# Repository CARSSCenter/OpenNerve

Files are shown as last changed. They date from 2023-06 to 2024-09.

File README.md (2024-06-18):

# OpenNerve
This repository contains all files relevant to the design and manufacture of the CARSS OpenNerve Platform. For more information about the CARSS Center, visit our [website](https://sites.usc.edu/carss/). Documentation, explanations of files, and protocols for fabrication, testing, and inspection can be found in the associated [wiki](https://github.com/CARSSCenter/Admin/wiki).

# License
Unless otherwise specified, all information and documents found in this repository are licensed under the Creative Commons CC-BY-4.0 license.

Shield: [][cc-by]

This work is licensed under a
[Creative Commons Attribution 4.0 International License][cc-by].

[][cc-by]

[cc-by]: http://creativecommons.org/licenses/by/4.0/
[cc-by-image]: https://i.creativecommons.org/l/by/4.0/88x31.png
[cc-by-shield]: https://img.shields.io/badge/License-CC%20BY%204.0-lightgrey.svg

# Disclaimer
The contents of this repository are subject to revision. No representation or warranty, express or implied, is provided in relation to the accuracy, correctness, completeness, or reliability of the information, opinions, or conclusions expressed in this repository.

The contents of this repository (the “Materials”) are experimental in nature and should be used with prudence and appropriate caution. Any use is voluntary and at your own risk.

The Materials are made available “as is” by USC (the University of Southern California and its trustees, directors, officers, employees, faculty, students, agents, affiliated organizations and their insurance carriers, if any), its collaborators Med-Ally LLC and Medipace Inc., and any other contributors to this repository (collectively, “Providers”). Providers expressly disclaim all warranties, express or implied, arising in connection with the Materials, or arising out of a course of performance, dealing, or trade usage, including, without limitation, any warranties of title, noninfringement, merchantability, or fitness for a particular purpose.

Any user of the Materials agrees to forever indemnify, defend, and hold harmless Providers from and against, and to waive any and all claims against Providers for any and all claims, suits, demands, liability, loss or damage whatsoever, including attorneys' fees, whether direct or consequential, on account of any loss, injury, death or damage to any person or (including without limitation all agents and employees of Providers and all property owned by, leased to or used by either Providers) or on account of any loss or damages to business or reputations or privacy of any persons, arising in whole or in part in any way from use of the Materials or in any way connected therewith or in any way related thereto.

The Materials, any related materials, and all intellectual property therein, are owned by Providers.

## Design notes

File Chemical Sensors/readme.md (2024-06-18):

The chemical sensors include sensors to measure concentrations of acetylcholine (ACh), catecholamines such as dopamine, serotonin, and norepinephrine, and pH levels in the body. They are being developed at USC in the laboratory of [Dr. Maral Mousavi](https://sites.usc.edu/mousavi/).

Contributors: Mona Abdelmonem, Farbod Amir, Ali Soleimani, Maral Mousavi

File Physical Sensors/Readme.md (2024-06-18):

The Strain and Temperature sensors are being developed at USC in the laboratory of [Dr. Hangbo Zhao](https://sites.usc.edu/zhaogroup/).

Contributors: Xinghao Huang, Xuan Li, Hangbo Zhao

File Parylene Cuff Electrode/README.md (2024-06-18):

The Parylene C cuff electrode is designed for branch nerves less than 1mm in diameter. Design, fabrication, and testing are performed at USC at the [Biomedical Microsystems Laboratory](http://biomems.usc.edu/) of Dr. Ellis Meng.

Contributors: Brianna Thielen, Alberto Esteban Linares, Quentin Rezard, Ellis Meng

Please see the [Design](https://github.com/CARSSCenter/Device/tree/main/Parylene%20Cuff%20Electrode/Design) folder for design files and the [Fabrication and Packaging](https://github.com/CARSSCenter/Device/tree/main/Parylene%20Cuff%20Electrode/Fabrication%20and%20Packaging) folder for fabrication instructions (beginning with the "Full Fabrication Protocol", which references the "Thin Film Fabrication Protocol").

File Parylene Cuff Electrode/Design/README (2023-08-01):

All mask designs are included in a single DXF file as separate layers (metal, electrodes+edge, edge only)
- DXF units are microns
- The overall mask size is 5" x 5" square for lithography on a 4" wafer
- Designs are summarized in the accompanying PDF
- Built in AutoCAD 2022 S.51.0.0

All 3D renderings do not include metal patterning (only the Parylene backbone is modeled)
- STEP units are millimeters
- SLDPRT files include three configurations: flat (prior to thermoforming), 0.5 or 0.7 mm (thermoformed size), and 0.8 or 1.0 mm (largest implanted size)
- Built in SolidWorks Professional 2019 SP5.0

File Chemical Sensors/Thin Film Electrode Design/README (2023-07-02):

This folder contains files describing the design and manufacture of the thin-film Parylene C - Platinum electrodes used for testing the acetylcholine, catecholamine, pH, counter, and reference electrodes on the benchtop.
For initial tests, these electrodes were fabricated at the PIE Foundry at USC: https://piefoundry.usc.edu/

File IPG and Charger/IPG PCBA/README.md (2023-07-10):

# Overview

This folder contains files and information around the Printed Circuit Board contained inside the Implantable Pulse Generator (IPG). This PCB was designed for CARSS by [Medipace Inc.](https://www.medipaceinc.com/). Editable source files, generated using Altium, can be found in the Source Files folder.

# Design
The purpose of this PCBA is to regulate power, communication, neuromodulation, and biomarker sensing. For a detailed description of the circuit design, please see the [associated wiki page](https://github.com/CARSSCenter/Admin/wiki/PCBA).

# Status and updates
## 29 June 2023
The first revision of the PCBA has been taped out and assembled; testing is expected to be finished by the end of 2023.

Test Board rev1

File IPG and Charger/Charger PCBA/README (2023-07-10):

The charger PCBA is still under development

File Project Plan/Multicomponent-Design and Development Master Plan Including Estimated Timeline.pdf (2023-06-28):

Nest 1 3 - Multicomponent
Design and Developmet Master Plan Including Estimated Timeline
Task | Scheduled Completion Date | Comments
Year 1 | Nest 1 & 3 Combined
| Master Plan - Med-Ally | June-23
| Provide all related documents for deliverables | June-23
| Nest 1
| System Requirements Nest 1 | June-23
| Develop test Plans for proposed tests | June-23
| First Design of IPG and Charger | June-23
| Design Review - IPG | June-23
| Nest 3
| System Requirements Nest 3 | June-23
| First Design of PDMS cuff, SNS, EMG, ECG, and AMS leads | June-23
Year 2 | Nest 1 & 3 Combined
| Provide all related documents for deliverables | June-24
| Nest 1
| Develop test protocols for IPG mechanical tests | January-24
| Build IPG prototypes | January-24
| Complete mechanical testing for IPG and charger | June-24
| Nest 3
| Develop test plans for leads | February-24
| Develop custom test fixtures for leads | February-24
| Develop Test Protocols for Leads | June-24
| Build Lead prototypes | June-24
Year 3 | Nest 1 & 3 Combined
| Provide all related documents for deliverables | June-25
| Nest 1
| Build IPG prototypes | June-25
| Nest 3
| Complete Lead testing | February-25
| Build Lead prototypes | June-25

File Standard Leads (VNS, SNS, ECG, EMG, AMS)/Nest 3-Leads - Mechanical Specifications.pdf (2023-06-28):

### Nest 3 – Leads

Mechanical Specifications

Page 1 of 9

### 1.0 Purpose

The purpose of this document is to provide product specifications for applicable Hornet Lead Package

### 2.0 Scope

In scope for this document are the product specifications inclusive to the Hornet IPG and charger; as part of the CARSS program Nest 3. The CARSS program stands for Center for Autonomic Nerve Recording and Stimulation Systems. The CARSS is part of the NIH Human Open Research Neural Engineering Technologies (HORNET) initiative for open-architecture, open-source implantable neuromodulation system. This includes a collaborative team between University of Southern California (USC, Los Angeles, CA), Medipace Inc (Pasedena, CA), and Med-Ally, LLC (Goose Creek, SC). The purpose of the system which the IPG and charger is a portion of is to enable community-supported neurotechnology platform to remove technical and financial hurdles to getting access to implantable neuromodulation technologies. Nest 3 focuses on a set of 5 standard leads: SNS, PDMS cuff, ECG, EMG, and AMS lead.

### 3.0 Definitions

Abbreviation | Definition
BLE | Bluetooth Low Energy. Operates on frequencies: 2.400 GHz – 2.4835 GHz
Controller | A computing device capable of running the NBS-EPG and IPG Controller application(s) tailored for physicians, the patient, or researchers.
IPG | Implantable Pulse Generator
HW | Hardware
SW | Software
PCB | Printed Circuit Board
PSD | Product Specifications Document
GUI | Graphical User Interface

Lead Mechanical Specifications
Page 2 of 9

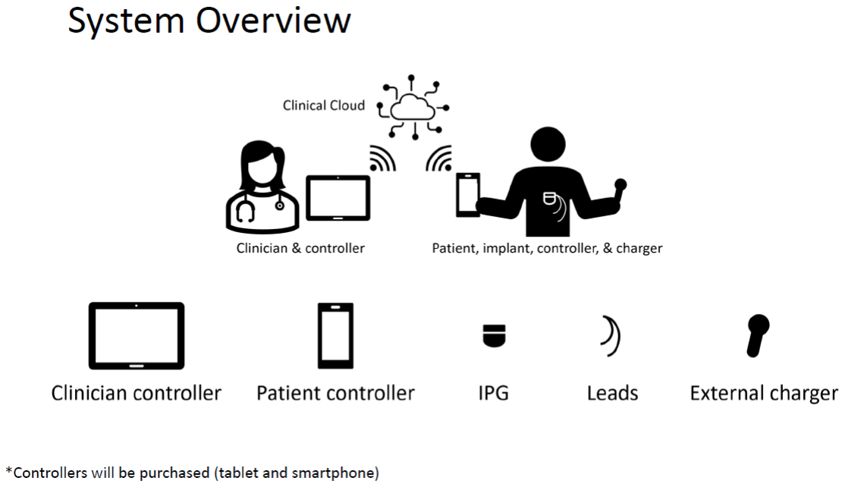
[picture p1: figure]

CONFIDENTIAL
All information contained in this document is confidential and is the sole property of Med-Ally Inc. Any reproduction in part or whole without the written permission of Med-Ally Inc. is prohibited.
Abbreviation | Definition
HIPAA | Health Insurance Portability and Accountability Act of 1996. U.S. legislation that provides data privacy and security for safeguarding medical information.
Wi-Fi | A facility allowing an electronic device to wirelessly transfer data or connect to the Internet using IEEE 802.11 standards. Operates on frequencies: 900 MHz, 2.4 GHz, 4.9 GHz, 5 GHz, 5.9 GHz and 60 GHz.
NIH | National Institute for Health
CARRS | Center for Autonomic Nerve Recording and Stimulation Systems
Hornet | Human Open Research Neural Engineering Technologies
Nest | Major component or module of the CARRS system

### 4.0 General Description of Product

The CARRS system is an open source system to enable developments in stimulation and sensing technologies. The system is capable of closed loop stimulation and sensing or can be used independently. The system components are: external charger and controller, implantable pulse generator, collection of interoperable and implantable leads.

Each portion of the CARSS system has been split into major components called nests. See

Page 3 of 9

figure below for details of major components or modules of the CARRS system:

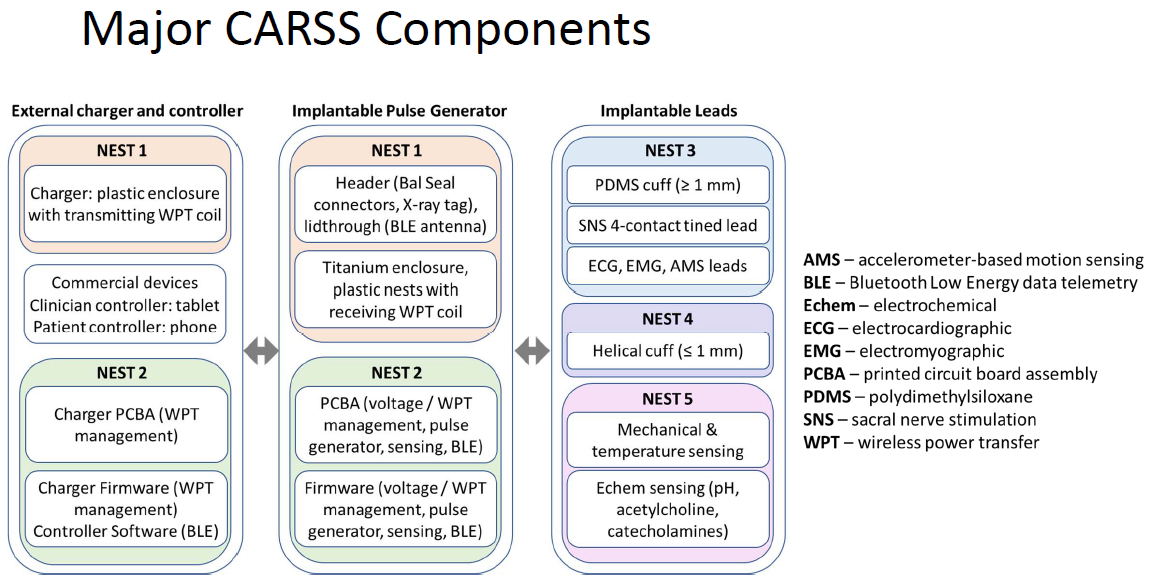
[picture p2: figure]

This document will only address Nest 1.
The IPG and charger for the CARRS system will be designed with the following engineering design principles as applicable:
- Material and component selection for maximizing the performance.
- Long-term reliability, redundancy, and fail-safe operations.
- Modularity, plug-and-play operation and off-the-shelf components.
- Preference for simpler and proven solutions over more complex and higher-risk ones.

### 6.0 Specifications

6.1 Leads Mechanical Specifications
PRD ID | Category | Specification Text
PRD-LDS-0001 | All | The leads are provided in the following lengths: 35 cm

Page 4 of 9

PRD ID | Category | Specification Text
| | 50 cm 50 cm 70 cm
PRD-LDS-0002 | All | The outside diameter of the leads shall be 1.27 mm diameter
PRD-LDS-0003 | All | The SNS, PDMS cuff, EMG, ECG, and AMS lead have 2 or 4 filar coiled leads with 0.70 mm pitch or greater.
PRD-LDS-0004 | All | The SNS, PDMS cuff, EMG, ECG, interconnect and AMS lead wire diameter is .102 mm/ 0.004” with 0.0127 mm/0.0005” thick coating.
PRD-LDS-0005 | All | The proximal contacts have 1.5mm length contacts.
PRD-LDS-0006 | All | The proximal set screw contact is 3mm in length.
PRD-LDS-0007 | All | Tines and trumpet anchor for anchoring can be added for each lead as needed.
PRD-LDS-0008 | All | The each connector utilizes a mechanism that holds the inserted lead in place. (e.g. set screw)
PRD-LDS-0009 | All | All the materials of the Lead Kit that are in contact with the body have been selected as known biocompatible.
PRD-LDS-0010 | All | The primary components for the Leads and interconnects shall be fabricated from the following materials: • Lead Body: Polyurethane, Pellethane 2363-55D • Proximal Inner Tube: PEEK • Distal Inner Tube: Polyurethane, Pellethane 2363-80A • Distal Electrodes: Platinum-Iridium (90/10) • Proximal Contacts: MP35N • Conductor Cable: PTFE coated Platinum-Iridium (80/20) • Setscrew: Titanium • Connector Block: MP35N

Page 5 of 9

PRD ID | Category | Specification Text
| | • Bal Seal connectors: MP35N and Pt-Ir • Silicone molded components Silicone Rubber -Med-4850, or similar • Connector block and set screw: 316L stainless steel • Misc Adhesives: Epoxy - Epotek 301, Silicone Rubber - Med-2000, urethane adhesive, silicone adhesive MED3-4213 • Suture: polypropylene or silk • Tines: pellethane • Suture Needle, crimp tubes: 316L Stainless Steel
PRD-SNS-0001 | SNS | SNS leads have electrodes on the distal end that are 3 mm in length with 3 mm space between electrodes
PRD-SNS-0002 | SNS | Up to 4 tines in series are added to the lead body to aid in lead retention and stability in vivo.
PRD-SNS-0003 | SNS | The lead systems incorporates a radio-opaque marker at the distal array in the form of platinum electrodes
PRD-SNS-0004 | SNS | The leads with a stylet inserted is able to pass completely through an 18-gauge needle
PRD-INT-0001 | Interconnect | The distal connector of the interconnect incorporates a connector block and set screw for securing the lead to the connector
PRD-INT-0002 | Interconnect | The distal connector of the interconnect accommodates two bipolar male connectors.
PRD-INT-0003 | Interconnect | The proximal connector of the interconnect interfaces with a quadipolar Sygnus Neuro Bal Seal connector in the IPG header.
PRD-INT-0004 | Interconnect | The interconnect connection portion is smaller than 0.5” X 1.5” X 0.5”
PRD-EMG-0001 | EMG | The EMG lead incorporates a Suture style needle

Page 6 of 9

PRD ID | Category | Specification Text
PRD-EMG-0002 | EMG | The EMG lead incorporates a suture connecting the needle to the stimulating portions of the lead
PRD-EMG-0003 | EMG | The EMG lead contains a single stimulating or sensing electrode
PRD-EMG-0004 | EMG | The EMG lead contains a Tumpet anchor to anchor electrode in place
PRD-EMG-0005 | EMG | The EMG lead interfaces with the bipolar connection.
PRD-EMG-0006 | EMG | The insertion needle length on the EMG lead is 32 mm
PRD-ECG-0001 | ECG | The ECG lead has two electrodes that can be 3mm to 100 mm apart.
PRD-ECG-0002 | ECG | The ECG lead has two anchor points: one at the end of the lead and the second proximal to the first electrode
PRD-ECG-0003 | ECG | The ECG lead interfaces with the bipolar connection
PRD-CUF-0001 | Cuff | The cuff electrode will have an inner diameter that accommodates nerves 2.5-5.5 mm in diameter – nominally 3.58 mm nerve.
PRD-CUF-0002 | Cuff | Cuff leads shall have two electrodes for bipolar stimulation.
PRD-CUF-0003 | Cuff | Cuff length along the nerve is 10 mm
PRD-CUF-0004 | Cuff | Lead exits cuff parallel to nerve
PRD-CUF-0005 | Cuff | Cuff electrode spacing is 2.5mm
PRD-CUF-0006 | Cuff | Electrodes are located 2.25mm inboard from edge of cuff
PRD-CUF-0007 | Cuff | Silicone cuff thickness is 1 mm
PRD-CUF-0008 | Cuff | Cuff includes dual sutures 35 mm long and 0.2mm diameter

Page 7 of 9

6.2 Testing Requirements
PRD ID | Specification Text
PRD-LDS-0011 | The leads contacts are electrically isolated to prevent interference between signals.
PRD-LDS-0012 | The Leads and Extensions shall be designed to withstand the following flexure cycles: -The Lead and Extension Connector shall withstand a minimum of 82,000 flex cycles. -The Lead and Extension body sections shall withstand a minimum of 47,000 flex cycles. Reference: EN45502-2-1 CENELEC Standard for Brady Pacemakers Testing will be performed per EN4552-2-1/ISO14708-2: 23.5.
PRD-LDS-0013 | Once the lead is locked in place into the IPG port or extension with the set screw fully torqued, the retention force of the lead shall be 10 N minimum along the lead axis relative to the connector. This retention force may exceed the destructive pull force of the inserted lead. EN45501-1 section 23.6 / ISO 14708-2: 23.6
PRD-LDS-0014 | When a tensile force of 5N is applied for 2 seconds along the main axis the of the lead or extension the assembly must not electrically and/or mechanically fail. ISO 14708-2: 23.3
PRD-LDS-0015 | Lead Insertion/Withdrawal Force Connector: The insertion and withdrawal force of a lead connector array into the IPG port connector or lead Extension port shall not exceed 2.2 lbs (9.8 N).
PRD ID | Category | Specification Text
PRD-AMS-0001 | AMS | The AMS lead is a quadripolar lead
PRD-AMS-0002 | AMS | The AMS lead has three suture points to anchor AMS distal end

Page 8 of 9

PRD ID | Specification Text
PRD-LDS-0016 | The interface between the extension distal connector body and a connected component shall not electrically and/or mechanically fail when tensile force of 2.2 lbf (9.8N) is applied between the components or across theirinterface. Deformation of componentsis allowable. Fracture of tubing orseparation of tubing from a component is not allowable. Examples of tensile force arrangements between an attached component and the Extension body.
PRD-LDS-0017 | The resistance for each connection in the distal connector shall remain ≤1000 Ohms and must not mechanically fail when bent 45°±2° off the main axis in any direction ISO 14708-2: 6.2.3
PRD-LDS-0018 | All the leads in the Leads Kit shall observe industry standard wiring practices for this type of application. The contact female connectors at the distal end and male contacts at the proximal end shall be connected through a one-to-one connection.
PRD-LDS-0019 | The proximal contact arrays of the Lead shall withstand 20 insertion and withdrawal cycles into the connector on the interconnect cable without causing physical or functional damage to the Lead.
PRD-LDS-0020 | The proximal contact arrays of the Lead and Extension shall withstand 20 insertion and withdrawal cycles into the port connector on the IPG without causing physical or functional damage to the Lead.
PRD-LDS-0021 | The lead assemblies should be able to withstand (function after experiencing) the following:

Page 9 of 9

PRD ID | Specification Text
| Accelerated aging per ISO 14708-1:19-1
PRD-LDS-0022 | When the lead or Extension assembly is dry in air, the electrical leakage between conductors at 100 ± 5 Volts DC shall be ≤10 microamperes. ISO 14708-2: 16.1
PRD-LDS-0023 | When the lead or Extension assembly is dry in air, the electrical leakage from any conductor to the outside lead body at 1000 ± 50 Volts DC shall be ≤0.75 microamperes per mm². ISO 14708-2: 16.2

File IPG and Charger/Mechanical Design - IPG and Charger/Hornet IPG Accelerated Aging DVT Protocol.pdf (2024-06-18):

### Hornet IPG

### Accelerated Aging Test Protocol

Effective Date: | Rev: | Pg. 1 of 19

CONFIDENTIAL
All information contained in this document is confidential and is the sole property of Med-Ally Inc. Any reproduction in part or whole without the written permission of Med-Ally Inc. is prohibited

1 Purpose
This protocol prescribes methods and records results to ensure the Hornet IPG adheres to accelerated aging standards. This protocol is based on ISO standards with reference to specific methods established at Med-Ally. This protocol is intended to be edited to meet the needs of each project at the time of execution without requiring revision of the template.
2 Scope
This document details methods for verification testing to ensure the devices continue to meet standards and requirements for the anticipated lifecycle of the device, and forms to record testing results. Section 8, Approvals, is intended to be repeatedly completed as testing stages of accelerated aging or real time samples and functional testing is completed.
3 References
Document No. | Title
ISO 14708-1: 19-1 | Implants for surgery – Active implantable medical devices – Part 1: General requirements for safety, marking and for information to be provided by the manufacturer
BS EN ISO 11607-1:2020 | Packaging for terminally sterilized medical devices, Part 1: Requirements for materials, sterile barrier systems, and packaging
ASTM F1980-16 | Standard Guide for Accelerated Aging of Sterile Barrier Systems for Medical Devices

### 4 Appendices

Appendix: | Title
A | Characterization of Material
B | Accelerated Aging Interval Record
C | Performance Test Requirements
D | Performance Testing Record
E | Serial Number Log
F | Real Time Aging Record
G | Testing Deviation Log
H | Additional Notes Area (if required)

### 5 Definitions

### Hornet IPG

### Accelerated Aging Test Protocol

Effective Date: | Rev: | Pg. 2 of 19

CONFIDENTIAL
All information contained in this document is confidential and is the sole property of Med-Ally Inc. Any reproduction in part or whole without the
Abbreviation or Term | Definition
DVT | Design Verification Test
IPG | Implantable Pulse Generator
DUT | Device Under Test
TAA | The elevated temperature at which the aging study is conducted, and it may be based on the estimated storage temperature, estimated usage temperature, or both
AAF | Accelerated Aging Factor; a correlation between the number of real time days to the number of simulated accelerated days, where 1 AAF = X RT days (reference calculations in the protocol for more information)
AAT | The length of time the accelerated aging is conducted
TRT | Storage temperature of real-time aging (RT) samples that represent storage conditions
Q10 | An aging factor for 10 ⷪC increase or decrease in temperature
Tm | Temperature at which a material melts
Tg | Glass transition temperature
Tα | Alpha temperature, heat distortion temperature
RT | Storage time of samples at ambient conditions
RT# | Number of real time days; desired real time shelf life duration or interval
AATRT# | Number of Accelerated Aging days, representing (real time * AAF) days in an interval period
Morphology | Examples include glassy amorphous, semi-crystalline, highly crystalline, % crystallinity, size, shape, structure, etc.

### Hornet IPG

### Accelerated Aging Test Protocol

Effective Date: | Rev: | Pg. 3 of 19

CONFIDENTIAL
All information contained in this document is confidential and is the sole property of Med-Ally Inc. Any reproduction in part or whole without the

### 6 Testing Protocol

6.1 Per the applicable standards, accelerated aging methods shall be used to determine any effects the passage of time may have on packaging components. Product requirement documents will establish the anticipated lifecycle of the sterlie packaging system, and be used as guidance for accelerated aging parameters. Record the following information and perform calculations to determine accelerated aging parameters:

6.1.1 | The Hornet IPG PN: will be tested to simulate 2 years using accelerated aging.
6.1.2 | List of Device Materials and Heat sensitive components: Part Number: __________________________________ Part Number: __________________________________ Part Number: __________________________________ Part Number: __________________________________ Part Number:__________________________________ Part Number: __________________________________ Part Number: __________________________________ Part Number: __________________________________ Part Number: __________________________________ Part Number: __________________________________ Part Number:__________________________________ Part Number: __________________________________ Part Number: __________________________________ Part Number: __________________________________ Complete Appendix A, Characterization or Materials, for each part unique part number of the device.

### Hornet IPG

### Accelerated Aging Test Protocol

Effective Date: | Rev: | Pg. 4 of 19

CONFIDENTIAL
All information contained in this document is confidential and is the sole property of Med-Ally Inc. Any reproduction in part or whole without the
Initial:__________________________ | Date:__________________________
6.1.3 | Long Term Storage Ambient Temperature* (TRT): 37 ⷪC
6.1.4 | Accelerated Aging Temperature* (TAA) : 55 ⷪC
6.1.5 | Q Factor* (Q10): 2.0
*Use 2.0 unless otherwise specified 6.1.6 Calculate Accelerated Aging Factor. Where: AAF = Accelerated Aging Factor
TAA = Accelerated Aging Temperature TRT = Ambient storage Temperature Q10 = Q Factor

AAF = Q10 [(TAA – TRT)/10]

AAF = 2.0[ ( 55 minus 37) divided by 10)] AAF = 2.0[ (18) divided by 10)]
AAF = 2.0[ 1.8 ]
AAF = 3.48 Days
6.1.7 | Desired Real Time Intervals (RT#):
| RT1: 90 Days (3 months) RT2: 182 Days (6 months) RT3: 365 Days (12 Months) RT4: 730 Days (24 Months) RT5: 1095 Days (36 Months) RT6: 1460 Days (48 Months) RT7: 1825 Days (60 Months)
6.1.8 | Accelerated Aging Time (AAT) for each Desired Real Time interval (Round to nearest
whole number):
| RT1 = 90 AATRT1 = RT1 Days / AAF AATRT1 = 90 divided by 3.48 AATRT1 = 26 Days
| RT2 = 183 AATRT2 = RT2 Days / AAF

### Hornet IPG

### Accelerated Aging Test Protocol

Effective Date: | Rev: | Pg. 5 of 19

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

AATRT2 = 183 divided by 3.48
AATRT2 = 53 Days

RT3 = 365
AATRT3 = RT3 Days / AAF
AATRT3 = 365 divided by 3.48 AATRT3 = 105 Days
RT4 = 730
AATRT4 = RT4 Days / AAF
AATRT4 = 730 divided by 3.48
AATRT4 = 210 Days

Print a copy of Appendix B, Accelerated Aging Interval Record, and complete the AAT information (top portion) for each desired interval required. Print an additional copy for RT0, to establish baseline testing results.

Initial:_______________________ | Date:________________________
6.1.9 | Performance Testing Requirements:
Complete Appendix C, Performance Test Requirements, to outline the tests to be performed by all accelerated and real time performance testing. Tests selected for evaluation should challenge the materials or device functionality that is most critical or most likely to fail as a result of aging.
Initial:____________________ | Date:___________________

6.2 Document the required number of RT samples below:

Total Real Time Sample Number:__________________________

Complete a copy of Appendix F for all Reat Time Aging test intervals, top portion only. Initial:____________________________ Date:_________________________

6.3 Total Sample Number:__________________________, as required per XXXX Hornet IPG and Charger Test Plan

### Hornet IPG

### Accelerated Aging Test Protocol

Effective Date: | Rev: | Pg. 6 of 19

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

6.4 Finished Device Drawing Number(s):__________________________________________

Initial:__________________ Date:_________________
6.5 Approval:

A representative from QA must review and approve the specification information to ensure accuracy of test protocol.

Quality Review Checklist:

Life-cycle Requirements | Initial____________ | Date:________________

Appendix A (Initial & Date on form) Qty:__________ Initial____________Date:________________

AAF Calculation Verification | Initial____________ | Date:________________
Desired RT Interval Verification | Initial____________ | Date:________________
AATRT# Calculation Verification | Initial____________ | Date:________________
Sample Number Verification | Initial____________ | Date:________________

Appendix B (Top Portion) Qty:__________ Initial____________Date:________________
Appendix C Performance Test Requirements | Initial____________ | Date:______________
Appendix F Real Time Aging Record (Top Portion) Initial____________ | Date:______________

Notes:_____________________________________________________________________

__________________________________________________________________________

__________________________________________________________________________

__________________________________________________________________________

Quality Approval to Execute Testing:

Signature:______________________________________ Date:_____________________

### Hornet IPG

### Accelerated Aging Test Protocol

Effective Date: | Rev: | Pg. 7 of 19

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

Due to duration of testing and costs, customer review and approval is required prior to starting Accelerated Aging. Customer Approval:
Print Name:____________________________________________

Position:__________________________________________

Signature:______________________________________ Date:_____________________ 6.6 Sample Generation

6.6.1 Describe the origin of the samples used. If new samples where created for this test, describe any deviations, if applicable, that may impact testing. Include work order number if available.

| ____________________________________________________________________
| ____________________________________________________________________
| ____________________________________________________________________
| ____________________________________________________________________
| ____________________________________________________________________
| ____________________________________________________________________
| ____________________________________________________________________
| ____________________________________________________________________
| ____________________________________________________________________
| ____________________________________________________________________
| ____________________________________________________________________
| ____________________________________________________________________
| Initial:___________________ Date:__________________

### Hornet IPG

### Accelerated Aging Test Protocol

Effective Date: | Rev: | Pg. 8 of 19

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

6.7 Sterilization
6.7.1 Submit all samples for sterilization per standard procedure:

Work Instruction:____________________________________

Shipping Date:______________________________________

Initial:_____________________ | Date:____________________
6.7.2 | Perform visual inspection on all samples for anomalies, damage, and paperwork
completeness. Attach sterilization records to this protocol.

Post Sterilization Return Date:______________________

Visual Inspection- Initial:_____________________ Date:_________________

Paperwork Verification- QA Initial:____________________Date:________________ 6.8 Equipment Information:

Controlled Environment Chamber or Bath:_________________________

Temperature Controller:________________________

Last Cal:__________________________ Cal Due:___________________

Timer:____________________________

Last Cal:__________________________ Cal Due:___________________

Thermal Logger:____________________________

### Hornet IPG

### Accelerated Aging Test Protocol

Effective Date: | Rev: | Pg. 9 of 19

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

Last Cal:__________________________ Cal Due:___________________

Notes:______________________________________________________________

____________________________________________________________________

____________________________________________________________________

____________________________________________________________________

Initial:_____________ Date:_______________
6.9 | Accelerated Aging and Real Time Testing:
6.9.1 | Complete Appendix D, Serial Number Log to designate devices for their intended testing
purpose. Reference the Testing Protocol section for required sample numbers in each category.
| Operator Initial:___________________ Date:____________________
6.9.2 | Place all real time samples into storage location. Record the Start date, andticipated
finsh date, and initial and date on all Appendix F, Real time Aging records to record real time aging initiation.
| Operator Initial:___________________ Date:____________________
6.9.3 | Place all accelerated aging samples into the BATH 0.9% sodium chlorine, ensuring the
temperature setpoint matches requirements. Record the Actual Start Date and Anticipated Finish Date for all Appendix B, Accelerated Aging Interval Record for all AATRT# forms to record accelerated aging initiation. Ensure thermologger is recording data at a rate >= 1 sample per minute.
Solution Part Number:_____________________________

Solution Lot Number:______________________________

Solution Expiration Date:___________________________

### Hornet IPG

### Accelerated Aging Test Protocol

Effective Date: | Rev: | Pg. 10 of 19

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

Operator Initial:___________________ Date:____________________

6.9.4 RT0 devices, as designated by Appendix E, Serial Number Log, may be tested immediately per requirements of Appendix C, Performance Testing Requirements, and recorded on the form in Appendix D, Performance Testing Record. Attach any reports generated by required testing to Appendix D, and submit the forms to QA for review upon completion.

Operator Initial:___________________ Date:____________________

6.9.5 Enter the Next Anticipated completion dates for AATRT# and RT#. Upon completion of required durations, review data logs to ensure accelerated aging devices have completed the required time period. Print an attach verification data to this protocol as it becomes available. Complete copies of Appendix D, Performance Testing Record for each batch of parts that meet accelerated or real time aging required durations.
In the event of power disruptions or data loss, complete Appendix G, Testing Deviation Record, to amend the duration requirements and change the anticipated completion dates.
Note: An NCR is NOT required if time is extended equal to the power out period or period of data loss if the deviation form is completed and attached, and no risk from the adverse event is expected to impact device performance.

The steps in this section shall be repeated until all aging durations are completed, and reviewed in the Approvals section.

### Hornet IPG

### Accelerated Aging Test Protocol

Effective Date: | Rev: | Pg. 11 of 19

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

### 7 Approvals –

### Note: This approval page is intended to be completed for each Accelerated Aging or

Real time data set. Release the protocol and up-rev with each completed aging stage.

### 7.1 Describe the functional testing stage being completed (AAT=RTx; Rtx, Etc):

### ____________________________________________________________

### ____________________________________________________________

### 7.2 Verify testing results meet drawing requirements and test standards

### Initial___________________ Date________________ 7.3 Quality Approval

7.3.1 | Review Protocol Completeness
7.3.2 | Review Appendix A: Characterization of Material
7.3.3 | Review Appendix B: Accelerated Aging Interval Record
7.3.4 | Review Appendix C: Performance Testing Requirements
7.3.5 | Review Appendix D: Performance Testing Record
7.3.6 | Review Appendix E: Serial Number Log
7.3.7 | Review Appendix F: Real Time Aging Record
7.3.8 | Review Appendix G: Testing Deviation Record
7.3.9 | Review Appendix H: Additional Notes

### 7.3.10 Ensure records support all required real time and accelerated aging

durations.

### Signature:_______________________________ Date:_____________________ 7.4 Other Approval (If required):

### Signature:_______________________________ Date:_____________________ 7.5 Notes (if required): _________________________________________________________________

### _________________________________________________________________

### _________________________________________________________________

### _________________________________________________________________

### Hornet IPG

### Accelerated Aging Test Protocol

Effective Date: | Rev: | Pg. 12 of 19

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

### Appendix A: Characterization of Material

### Part Number:_______________________________

### Part Description:_____________________________

### Composition:________________________________________________________________

### Morphology:________________________________________________________________

Tm=___________ ⷪC | Tg=___________ ⷪC | Tα=___________ ⷪC

Additive, processing agents, catalysts, lubricants, residual solvents, corrosive gasses, and

### fillers, or other notes:

### __________________________________________________________________________

### __________________________________________________________________________

### __________________________________________________________________________

### __________________________________________________________________________

### __________________________________________________________________________

### __________________________________________________________________________

### __________________________________________________________________________

### __________________________________________________________________________

### Suggested Max Temperature:_________________ ⷪC

### Signature:_________________________________ Date:______________________

### QA Initial:________________________ Date:______________________

### Hornet IPG

### Accelerated Aging Test Protocol

Effective Date: | Rev: | Pg. 13 of 19

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

### Appendix B: Accelerated Aging Interval Record

### Finished Assembly Drawing Number:______________________________________

### AATRT#:__________________________ Real Time Duration:___________________days

### Accelerated Aging Time:____________days Sample Number:____________

### Temperature Set Point:_____________

### Print Name:______________________________________________________

### Signature:__________________________________ Date:______________________

### Actual Start Date:_______________________ Initial:____________ Date:___________

### Anticipated Finish Date:_______________________

### Deviations:

### __________________________________________________________________________

### Notes: __________________________________________________________________________

### __________________________________________________________________________

Finish Date:_______________________ | Sample Number:____________
Attach Thermologger Data (Check): ____ | Total Accelerated Aging Time:___________

### Minimum Duration at Accelerated Temperature Verified (check): ____

### Print Name:______________________________________________________

### Signature:__________________________________ Date:______________________

### Hornet IPG

### Accelerated Aging Test Protocol

Effective Date: | Rev: | Pg. 14 of 19

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

### Appendix C: Performance Testing Requirements

### Visual Inspection Requirements: __________________________________________________________________________

### __________________________________________________________________________

### __________________________________________________________________________

### __________________________________________________________________________

### __________________________________________________________________________

### Functional Testing Requirements: __________________________________________________________________________

### __________________________________________________________________________

### __________________________________________________________________________

### __________________________________________________________________________

### __________________________________________________________________________

### Bench Testing Requirements: __________________________________________________________________________

### __________________________________________________________________________

### __________________________________________________________________________

### __________________________________________________________________________

### __________________________________________________________________________

### Operator Signature:____________________________ Date:__________________________

### Quality Signature:______________________________ Date:____________Page___ of____

### Hornet IPG

### Accelerated Aging Test Protocol

Effective Date: | Rev: | Pg. 15 of 19

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

### Appendix D: Performance Testing Record

### Serial Number

### Visual Inspection Pass/ NCR#

### Functional Inspection Pass/ NCR#

### Bench Testing Pass/ NCR#

### Notes:

### Operator Signature:____________________________ Date:__________________________

### Quality Signature:______________________________ Date:____________Page___ of____

### Hornet IPG

### Accelerated Aging Test Protocol

Effective Date: | Rev: | Pg. 16 of 19

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

### Appendix E: Serial Number Log

Serial Number | Select One | RT# | Testing Duration (Days) | Start Date
Accelerated Aging | Real Time Aging

### Operator Signature:____________________________ Date:__________________________

### Quality Signature:______________________________ Date:____________Page___ of____

### Hornet IPG

### Accelerated Aging Test Protocol

Effective Date: | Rev: | Pg. 17 of 19

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

### Appendix F: Real-Time Aging Record

### Finished Assembly Drawing Number:______________________________________

### RT#:____________________________Duration:___________________days

### Sample Number:____________ Ambient Start Temperature: ________

### Print Name:______________________________________________________

### Signature:__________________________________ Date:______________________

### Start Date:_______________________Anticipated Finish Date:____________

### Initial:___________________________Date:_________________

### Deviations:

### __________________________________________________________________________

### __________________________________________________________________________

### Notes: __________________________________________________________________________

### __________________________________________________________________________

### __________________________________________________________________________

### Ambient Finish Temperature:______________________

### Actual Finish Date:_______________________ Sample Number:____________

### Total Time Elapsed:_________________ days

### Print Name:______________________________________________________

### Signature:__________________________________ Date:______________________

### Hornet IPG

### Accelerated Aging Test Protocol

Effective Date: | Rev: | Pg. 18 of 19

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

### Appendix G: Testing Deviation Record

### Date of Deviation:_______________________________________

### Cause of Deviation:_________________________________________________________

### __________________________________________________________________________

### __________________________________________________________________________

### Current RT#:____________

### End of Deviation Date:__________________________________

### Prior anticipated RT# Aging Completion Date:_________________________

### New anticipated RT# Aging Completion Date:__________________________

### NCR:____________________________ if applicable*

*NCR is not required if the only impact is completion extension.

### Engineer Name:_____________________________

### Engineer Signature:__________________________ Date:______________________

### QA Representative Name:____________________________________

### QA Signature:_______________________________ Date:______________________

### Hornet IPG

### Accelerated Aging Test Protocol

Effective Date: | Rev: | Pg. 19 of 19

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

### Appendix H: Additional Notes (if required). Notes may be typed or hand written:

### Signature:_____________________________ Date:____________ Page___ of____

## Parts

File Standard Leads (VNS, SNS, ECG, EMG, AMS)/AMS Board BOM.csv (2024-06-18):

Name | Description | Designator | Manufacturer 1 | Manufacturer Part Number 1
ZRB15XR61A106ME01D | Capacitor, 10uf, X5R, 10V, 20%, 0402, Implant-grade | C200 | Murata | ZRB15XR61A106ME01D
GCM155R71C104KA55 | Capacitor, 0.1uF, X7R, 16V, 10%, 0402, Implant-grade | C201 | Murata | GCM155R71C104KA55J
MIS2DHTR | Analog Circuit, Accelerometer, LGA-12 | U200 | STMicroelectronics | MIS2DHTR

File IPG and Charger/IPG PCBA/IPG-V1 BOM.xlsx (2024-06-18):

Quantity | Designator | Description | Manufacturer | Manufacturer Part Number
8 | C100, C101, C104, C105, C210, C211, C215, C219 | Ceramic Capacitor, Multilayer, Ceramic, 25V, 5% +Tol, 5% -Tol, C0G, 30ppm/Cel TC, 0.000012uF, Surface Mount, 0201 | Murata | GRM0335C1E120JA01D
15 | C102, C103, C115, C118, C119, C213, C306, C317, C319, C501, C503, C504, C600, C1201, C1203 | Capacitor, 4.7uF, X5R, 16V, 10%, 0603, Implant-grade | Murata | GRM188R61C475KE11
49 | C106, C107, C108, C109, C110, C111, C112, C113, C114, C116, C120, C214, C216, C307, C500, C502, C507, C508, C509, C510, C511, C512, C602, C700, C701, C702, C703, C704, C800, C801, C807, C808, C815, C816, C819, C820, C821, C822, C901, C903, C905, C908, C1101, C1200, C1202, C1204, C1207, C1300, C1301 | Ceramic Capacitor, Multilayer, Ceramic, 25V, 10% +Tol, 10% -Tol, X5R, 15% TC, 0.1uF, Surface Mount, 0201 | Murata | GRM033R61E104KE14J
7 | C117, C218, C400, C420, C1102, C1205, C1206 | Ceramic Capacitor, Multilayer, Ceramic, 16V, 20% +Tol, 20% -Tol, X5R, 15% TC, 1uF, Surface Mount, 0201 | Murata | GRM033R61C105ME15D
1 | C200 | Capacitor, 0.8pF, Silicon RF, 200V, Tolerance 0.05pF, 0402, Implant-grade | Kyocera AVX | 600L0R8AT200T
1 | C201 | Capacitor, 1pF, RF Capacitors, 200V, Tolerance 0.01pF, 0402, Implant-grade | Kyocera AVX | 600L1R0AT200T
1 | C217 | Ceramic Capacitor, Multilayer, Ceramic, 25V, 10% +Tol, 10% -Tol, X7R, 15% TC, 0.0001uF, Surface Mount, 0201 | Murata | GRM033R71E101KA01D
2 | C300, C301 | Capacitor, 27nF, C0G, 100VDC, 2%, 0805, Implant-grade | Murata | GRM2195C2A273GE01D
2 | C302, C303 | Capacitor, 4.7nF, C0G, 25V, 1%, 0603, Implant-grade | KEMET | C0603C472F3GECTU
1 | C304 | Ceramic Capacitor, Multilayer, Ceramic, 25V, 5% +Tol, 5% -Tol, C0G, 30ppm/Cel TC, 0.000033uF, Surface Mount, 0201 | Murata | GRM0335C1E330JA01D
5 | C310, C311, C318, C505, C506 | Capacitor, 4.7uF, X7S, 35V, 10%, 0805, Implant-grade | Murata | GCM21BC7YA475KE36L
2 | C315, C316 | Capacitor, 0.022uF, X7R, 50V, 10%, 0402, Implant-grade | Murata | GCM155R71H223KA55
2 | C417, C422 | Capacitor, 0.1uF, X7R, 16V, 10%, 0402, Implant-grade | Murata | GCM155R71C104KA55
2 | C419, C423 | Ceramic Capacitor, Multilayer, Ceramic, 25V, 10% +Tol, 10% -Tol, X7R, 15% TC, 0.00047uF, Surface Mount, 0201 | Murata | GCM033R71E471KA03D
1 | C601 | Capacitor, 10uf, X5R, 10V, 20%, 0402, Implant-grade | Murata | ZRB15XR61A106ME01D
2 | C802, C804 | Capacitor, 0.33uF, X7S, 16V, 10%, 0402 | TDK | CGA2B1X7S1C334K050BC
5 | C803, C805, C810, C814, C823 | Ceramic Capacitor, Multilayer, Ceramic, 25V, 10% +Tol, 10% -Tol, X7R, 15% TC, 0.001uF, Surface Mount, 0201 | Murata | GRM033R71E102KA01J
1 | C806 | Capacitor, 1500pF, X7R, 50V, 10%, 0402 | Murata | GCM155R71H152KA37D
2 | C809, C827 | Ceramic Capacitor, Multilayer, Ceramic, 6.3V, 20% +Tol, 20% -Tol, X5R, 15% TC, 1.5uF, Surface Mount, 0201 | Murata | GRM033R60J155ME14D
4 | C811, C812, C824, C825 | Capacitor, 470nF, X5R, 6.3V, 10%, 0201, Implant Grade | Murata | GRT033R60J474KE01D
2 | C813, C828 | 68 pF ±5% 50V Ceramic Capacitor C0G, NP0 0201 (0603 Metric) | Murata Electronics | GRM0335C1H680JA01D
2 | C817, C818 | Capacitor, 2.2uF, X7R, 16V, 10%, 0603, Implant-grade | Murata | GRM188Z71C225ME43J
2 | C826, C829 | 270 pF ±5% 25V Ceramic Capacitor C0G, NP0 0201 (0603 Metric) | Murata Electronics | GRM0335C1E271JA01D
9 | C900, C902, C904, C906, C907, C909, C910, C911, C912 | Capacitor, 10uF, X5R, 50V, 10%, 0805 | Murata | GRM21BR61H106ME43L
16 | C1000, C1001, C1002, C1003, C1004, C1005, C1006, C1007, C1008, C1009, C1010, C1011, C1012, C1013, C1014, C1015 | Capacitor, 680pF, C0G, 100V, 5%, 0402 | TDK | C1005C0G2A681J050BE
1 | C1016 | Capacitor, 68pF, C0G, 25V, 5%, 0201, Implant-grade | Murata | GRT0335C1E680JA02D
10 | D300, D301, D305, D306, D400, D420, D502, D503, D505, D506 | Schottky, 40V, 500mA, 530mV, SOD-523 | ON Semiconductor | NSR05T40XV2T5G
1 | D307 | Zener Diode 10 V 300 mW ±2% Surface Mount DFN1006-2A 0402 | Vishay | BZX884B10L-G3-08
7 | D419, D421, D422, D423, D424, D600, D601 | Schottky, 30V, 100mA, 385mV, 200mW, SOD-923 | ON Semiconductor | NSR0130P2T5G
16 | D800, D801, D802, D803, D804, D805, D806, D807, D808, D809, D810, D811, D812, D813, D814, D815 | Diode | Nexperia | BAS116LS-QYL
17 | D1000, D1001, D1002, D1003, D1004, D1005, D1006, D1007, D1008, D1009, D1010, D1011, D1012, D1013, D1014, D1015, D1016 | Diode ESD (Bi-directional) | Nexperia | PESD5V0S1BLD,315
2 | D1101, D1102 | ESD TVS DIODE 3.3VWM 6.2VC 0402C | Comchip Technology | CPDQC3V3T-HF
1 | D1201 | TVS DIODE 5.5VWM 6TSOP | Nexperia | IP4220CZ6F
1 | D1202 | LED, GREEN, SMD, 0603, 3.2V, 20mA | Lite-On Inc. | LTST-C191TGKT
1 | D1203 | LED, RED, SMD, 0603, 2V, 30mA | Lite-On Inc. | LTST-C191KRKT
1 | D1204 | LED, ORANGE, SMD, 0603, 2V, 30mA | Lite-On Inc. | LTST-C191KFKT
2 | F400, F401 | Fuse, 750mA, 63V, 1206 | Littelfuse | 0440.750WR
4 | J100, J102, J201, J202 | 0.025" SQ Post Header, Through-hole, Vertical, -55 to 125 degC, 2.54 mm Pitch, 6-Pin, Male, RoHS | Samtec | TSW-106-07-G-S
2 | J101, J200 | Connector, 1.27 mm, 2x5, Male, TH | Samtec | FTSH-105-01-F-D-K
1 | J203 | RF Connector, 1 Contact(s), Male, Board Mount, Surface Mount Terminal, Receptacle | Hirose | U.FL-R-SMT-1(10)
5 | J302, J421, J424, J1101, J1202 | Board Connector, 4 Contact(s), 1 Row(s), Male, Straight, 0.1 inch Pitch, Solder Terminal, Black Insulator, Receptacle | Samtec | TSW-104-07-G-S
17 | J1017, J1018, J1019, J1020, J1021, J1022, J1023, J1024, J1025, J1026, J1027, J1028, J1029, J1030, J1031, J1032, J1033 | Connector, Bannana Tip, Through Hole, Rodent Study lead connector | Cinch Connectivity Solutions Johnson | 105-0753-001
1 | J1201 | CONN RCP USB3.1 TYPEC 24P SMD RA | Molex | 1054500101
1 | L100 | Inductor, 2.2uH, 1.76A, 1008 | TDK | VLS252010HBX-2R2M-1
1 | L101 | Inductor, Unshielded, 33nH, 350mA, 0402 | Murata | LQG15HS33NJ02D
1 | L200 | Inductor, 3.9nH, 1.95A, 2%, 0402 | Murata | LQW15AN3N9G80D
1 | L201 | Inductor, 1.8nH, 0.46A, Tolerance 0.2 nH, 0402 | Murata | LQW15AN1N8C00D
2 | L300, L500 | Inductor, 10uH, 600mA, 20%, 1008 | Wurth | 74438323100
3 | M200, M314, M700 | MOSFET, P-chan, -20V, -383mA, DFN0604 | Diodes Inc | DMP22D4UFO-7B
4 | M300, M311, M312, M504 | MOSFET, N-Chan, 60V, 320mA, DFN1006 | Diodes Inc | DMN62D1LFB-7B
4 | M305, M308, M309, M501 | MOSFET, P-chan, -65V, -290mA, DFN1006 | Diodes Inc | DMP68D1LFB
5 | M306, M401, M402, M410, M411 | MOSFET, P-chan, -20V, -3.4A, DFN1010-3 | Diodes Inc | DMP2043UCA3-7
1 | M310 | MOSFET, N-Chan, 60V, 300mA, DFN1006 | Diodes Inc | DMN62D1SFB-7B
11 | M400, M405, M409, M412, M420, M421, M500, M505, M600, M601, M603 | MOSFET, P-chan, -20V, -400mA, X2-DFN1006-3 | Diodes Inc | DMP21D5UFB4-7B
26 | M403, M404, M406, M407, M408, M413, M414, M415, M416, M417, M418, M419, M422, M502, M503, M506, M602, M604, M701, M1300, M1302, M1305, M1306, Q1101, Q1102, Q1103 | MOSFET, N-Chan, 20V, 170mA, DFN0606 | Diodes Inc | DMN2990UFZ-7B
9 | M900, M901, M902, M903, M904, M905, M906, M907, M908 | MOSFET, N-Chan, 60V, 210mA, DFN1006 | Diodes Inc | DMN65D8LFB-7B
9 | Q900, Q902, Q904, Q906, Q907, Q911, Q913, Q915, Q917 | TRANS 2PNP 40V 0.2A SOT963 | ON Semi | NST3906DP6T5G
10 | Q901, Q903, Q905, Q908, Q909, Q910, Q912, Q914, Q916, Q918 | Transistor, NPN, 45V, 100mA, DFN1006 | Diodes Inc | BC847BLP-7B
8 | R100, R101, R404, R415, R510, R908, R1101, R1103 | Fixed Resistor, Metal Glaze/thick Film, 0.05W, 10000ohm, 30V, 1% +/-Tol, 200ppm/Cel, Surface Mount, 0201 | Vishay | CRCW020110K0FNED
13 | R102, R103, R359, R429, R430, R702, R708, R806, R821, R835, R857, R912, R1106 | Fixed Resistor, Metal Glaze/thick Film, 0.05W, 0ohm, Surface Mount, 0201 | Vishay | CRCW02010000Z0ED
30 | R310, R316, R317, R318, R320, R322, R324, R325, R328, R329, R330, R402, R403, R412, R414, R421, R422, R423, R424, R425, R426, R427, R428, R812, R813, R814, R845, R929, R931, R1208 | Fixed Resistor, Metal Glaze/thick Film, 0.05W, 1000000ohm, 30V, 1% +/-Tol, 200ppm/Cel, Surface Mount, 0201 | Vishay | CRCW02011M00FNED
1 | R315 | Fixed Resistor, Metal Glaze/thick Film, 0.05W, 402ohm, 30V, 1% +/-Tol, 200ppm/Cel, Surface Mount, 0201 | Vishay | CRCW0201402RFNED
1 | R319 | Fixed Resistor, Metal Glaze/thick Film, 0.05W, 49.9ohm, 30V, 1% +/-Tol, 200ppm/Cel, Surface Mount, 0201 | Vishay | CRCW020149R9FNED
3 | R323, R838, R861 | Fixed Resistor, Metal Glaze/thick Film, 0.05W, 150000ohm, 30V, 1% +/-Tol, 200ppm/Cel, Surface Mount, 0201 | Vishay | CRCW0201150KFNED
5 | R326, R500, R705, R829, R856 | Fixed Resistor, Metal Glaze/thick Film, 0.05W, 100000ohm, 30V, 1% +/-Tol, 200ppm/Cel, Surface Mount, 0201 | Vishay | CRCW0201100KFNED
51 | R336, R341, R400, R401, R408, R410, R411, R413, R502, R503, R504, R505, R509, R600, R601, R602, R603, R604, R703, R800, R801, R803, R804, R808, R809, R815, R819, R823, R824, R832, R833, R834, R836, R837, R846, R847, R848, R849, R903, R910, R916, R924, R925, R935, R940, R945, R950, R1300, R1302, R1304, R1306 | Fixed Resistor, Metal Glaze/thick Film, 0.05W, 10000000ohm, 30V, 1% +/-Tol, 200ppm/Cel, Surface Mount, 0201 | Vishay Draloric | CRCW020110M0FNED
3 | R337, R348, R356 | Fixed Resistor, Metal Glaze/thick Film, 0.05W, 49900ohm, 30V, 1% +/-Tol, 200ppm/Cel, Surface Mount, 0201 | Vishay | CRCW020149K9FNED
2 | R405, R416 | Fixed Resistor, Metal Glaze/thick Film, 0.05W, 4020ohm, 30V, 1% +/-Tol, 200ppm/Cel, Surface Mount, 0201 | Vishay | CRCW02014K02FNED
2 | R406, R417 | Fixed Resistor, Metal Glaze/thick Film, 0.05W, 7500ohm, 30V, 1% +/-Tol, 200ppm/Cel, Surface Mount, 0201 | Vishay | CRCW02017K50FNED
2 | R407, R419 | Resistor, 619k, 0.1%, 0402 | Vishay | MCS0402MD6193BE000
2 | R409, R420 | Resistor, 243k, 0.1%, 0402 | TE Connectivity | RP73PF1E243KBTDF
1 | R418 | Fixed Resistor, Metal Glaze/thick Film, 0.05W, 5100000ohm, 30V, 1% +/-Tol, 200ppm/Cel, Surface Mount, 0201 | Vishay Draloric | CRCW02015M10FNED
2 | R501, R928 | Fixed Resistor, Metal Glaze/thick Film, 0.05W, 100ohm, 30V, 1% +/-Tol, 200ppm/Cel, Surface Mount, 0201 | Vishay | CRCW0201100RFNED
1 | R506 | Fixed Resistor, Metal Glaze/thick Film, 0.05W, 340000ohm, 30V, 1% +/-Tol, 200ppm/Cel, Surface Mount, 0201 | Vishay | CRCW0201340KFKED
1 | R511 | Fixed Resistor, Metal Glaze/thick Film, 0.05W, 40200ohm, 30V, 1% +/-Tol, 200ppm/Cel, Surface Mount, 0201 | Vishay | CRCW020140K2FNED
2 | R700, R706 | Fixed Resistor, Metal Glaze/thick Film, 0.05W, 8200ohm, 30V, 1% +/-Tol, 200ppm/Cel, Surface Mount, 0201 | Vishay | CRCW02018K20FNED
2 | R701, R707 | Fixed Resistor, Metal Glaze/thick Film, 0.05W, 59000ohm, 30V, 1% +/-Tol, 200ppm/Cel, Surface Mount, 0201 | Vishay | CRCW020159K0FNED
1 | R704 | Fixed Resistor, Metal Glaze/thick Film, 0.05W, 120000ohm, 30V, 1% +/-Tol, 200ppm/Cel, Surface Mount, 0201 | Vishay Dale | CRCW0201120KFNED
1 | R802 | Fixed Resistor, Metal Glaze/thick Film, 0.05W, 1400000ohm, 30V, 1% +/-Tol, 200ppm/Cel, Surface Mount, 0201 | Vishay Draloric | CRCW02011M40FNED
8 | R805, R807, R820, R822, R839, R840, R850, R851 | Fixed Resistor, Metal Glaze/thick Film, 0.05W, 180000ohm, 30V, 1% +/-Tol, 200ppm/Cel, Surface Mount, 0201 | Vishay | CRCW0201180KFNED
4 | R810, R825, R841, R852 | Fixed Resistor, Metal Glaze/thick Film, 0.05W, 360000ohm, 30V, 1% +/-Tol, 200ppm/Cel, Surface Mount, 0201 | Vishay | CRCW0201360KFNED
1 | R811 | Fixed Resistor, Metal Glaze/thick Film, 0.05W, 2200000ohm, 30V, 1% +/-Tol, 200ppm/Cel, Surface Mount, 0201 | Vishay Draloric | CRCW02012M20FNED
2 | R816, R858 | Fixed Resistor, Metal Glaze/thick Film, 0.05W, 200000ohm, 30V, 1% +/-Tol, 200ppm/Cel, Surface Mount, 0201 | Vishay | CRCW0201200KFNED
4 | R817, R826, R853, R854 | 3.32 MOhms ±1% 0.05W, 1/20W Chip Resistor 0201 (0603 Metric) Thick Film | Vishay Dale | CRCW02013M32FNED
2 | R818, R855 | 475 kOhms ±1% 0.05W, 1/20W Chip Resistor 0201 (0603 Metric) Thick Film | Vishay Dale | CRCW0201475KFNED
2 | R827, R859 | 1.2 MOhms ±1% 0.05W, 1/20W Chip Resistor 0201 (0603 Metric) Thick Film | Vishay Dale | CRCW02011M20FNED
2 | R828, R860 | 3.74 kOhms ±1% 0.05W, 1/20W Chip Resistor 0201 (0603 Metric) Thick Film | Vishay Dale | CRCW02013K74FNED
2 | R830, R831 | Fixed Resistor, Metal Glaze/thick Film, 0.05W, 6800000ohm, 30V, 1% +/-Tol, 200ppm/Cel, Surface Mount, 0201 | Vishay Draloric | CRCW02016M80FNED
2 | R842, R843 | Fixed Resistor, Metal Glaze/thick Film, 0.05W, 2700000ohm, 30V, 1% +/-Tol, 200ppm/Cel, Surface Mount, 0201 | Vishay Draloric | CRCW02012M70FNED
1 | R844 | Fixed Resistor, Metal Glaze/thick Film, 0.05W, 249000ohm, 30V, 1% +/-Tol, 200ppm/Cel, Surface Mount, 0201 | Vishay | CRCW0201249KFNED
14 | R901, R906, R914, R919, R922, R933, R938, R943, R948, R1200, R1203, R1204, R1206, R1207 | Fixed Resistor, Metal Glaze/thick Film, 0.05W, 1000ohm, 30V, 1% +/-Tol, 200ppm/Cel, Surface Mount, 0201 | Vishay | CRCW02011K00FNED
9 | R902, R907, R915, R920, R923, R934, R939, R944, R949 | Fixed Resistor, Metal Glaze/thick Film, 0.05W, 150ohm, 30V, 1% +/-Tol, 200ppm/Cel, Surface Mount, 0201 | Vishay | CRCW0201150RFNED
9 | R904, R911, R917, R926, R927, R936, R941, R946, R951 | Fixed Resistor, Metal Glaze/thick Film, 0.05W, 2000000ohm, 30V, 1% +/-Tol, 200ppm/Cel, Surface Mount, 0201 | Vishay Draloric | CRCW02012M00FNED
1 | R930 | Fixed Resistor, Metal Glaze/thick Film, 0.05W, 2800ohm, 30V, 1% +/-Tol, 200ppm/Cel, Surface Mount, 0201 | Vishay | CRCW02012K80FNED
3 | R1102, R1104, R1105 | Fixed Resistor, Metal Glaze/thick Film, 0.05W, 6800ohm, 30V, 1% +/-Tol, 200ppm/Cel, Surface Mount, 0201 | Vishay | CRCW02016K80FNED
2 | R1201, R1202 | Fixed Resistor, Metal Glaze/thick Film, 0.05W, 5110ohm, 30V, 1% +/-Tol, 200ppm/Cel, Surface Mount, 0201 | Vishay | CRCW02015K11FNED
3 | R1205, R1210, R1211 | Resistor 200 1%, 0402, Non Implant-grade | Vishay | CRCW0402200RFKEDHP
2 | R1301, R1303 | Fixed Resistor, Metal Glaze/thick Film, 0.2W, 499ohm, 50V, 1% +/-Tol, 100ppm/Cel, Surface Mount, 0402 | Vishay Dale | CRCW0402499RFKEDHP
1 | SW500 | Pushbutton, NO-MOM, 12V, 0.05A, SMT | C&K | PTS647SN50SMTR2LFS
1 | U100 | FRAM, 8 Mbit (1024k x 8), SPI, 1.8-3.6V, QFN-8 | Cypress Semiconductor | CY15B108QN-20LPXC
1 | U101 | Microcontroller, ARM Cortex-M33, 2.0 MB Flash, 786 kB RAM, BGA-132 pins with dedicated pinout supporting SMPS step-down converter | STMicro | STM32U585QII6Q
1 | U200 | Bluetooth radio, v5.0, 192 kB Flash, 24 kB RAM, BGA-33 | Nordic | NRF52810-CAAA-E-R7
6 | U300, U302, U313, U314, U404, U405 | Op Amp, Rail-to-Rail, 95kHz, WLCSP-6 | Analog Devices | AD8505ACBZ-R7
1 | U315 | Buck-Boost Converter, Selectable Voltage, QFN-20 | Analog Devices | LTC3130IUDC-1#PBF
2 | U400, U402 | Charge Controller, 4.2V, 250mA, DFN-6 | Linear Technology | LTC4065LEDC#TRPBF
2 | U401, U403 | Comparator, 1.2V Reference, Open-drain, BGA-4 | Texas Instruments | TLV4021R1YKAR
3 | U500, U502, U504 | LDO Regulator, 3.3V, Shutdown, DFN1010-4 | Diodes Inc | AP7354D-33FS4-7
1 | U501 | Boost, SEPIC Switching Regulator IC Positive Adjustable 1.23V 1 Output 75mA (Switch) SOT-23-5 | Linear Technology | LT1615ES5-1#TRPBF
1 | U503 | Digital potentiometer, 256 taps, 100k, I2C, QFN-10 | Renesas | ISL23315TFRUZ-T7A
1 | U505 | Reset Monitor, 2.63V, Active low, X2SON | Texas Instruments | TPS3831L30DQNR
1 | U600 | Magnet Sensor, 15 Gauss, ULLGA4, Implant-grade | NVE | ADL021-14E
2 | U700, U701 | Multiplexer, 8:1, 0.7 ohms, QFN-16 | Maxim | MAX4781ETE+T
2 | U702, U905 | Op Amp, Dual, Rail-to-Rail, 1MHz, BGA-9 | Texas Instruments | TLV9002SIYCKR
1 | U703 | Differential Amplifier, 110 MHz, DFN-8 | Analog Devices | AD8137YCPZ-REEL7
1 | U704 | SPDT, 2 Func, 1 Channel, CMOS | Analog Devices | ADG772BCPZ-REEL7
2 | U800, U802 | Analog front end, ECG, RLD amp, BGA-20 | Analog Devices | AD8233ACBZ-R7
2 | U801, U803 | Analog Circuit, 1 Func, 1 Channel | Analog Devices | AD8232ACPZ-R7
1 | U900 | Monostable, RC set, dual triggers, BGA-8 | Texas Instruments | SN74LVC1G123YZPR
1 | U901 | AND gate, Dual 2-input, BGA-8 | Texas Instruments | SN74LVC2G08YZPR
1 | U902 | DAC, 16-bit, Dual channel, SPI/I2C, WSON-10 | Texas Instruments | DAC80502DRXT
3 | U903, U904, U1101 | Analog Switch, SPDT, 2:1, DSBGA6 | Texas Instruments | TS5A3159AYZPR
1 | U1201 | IC USB TO UART BRIDGE QFN20 | Silicon Labs | CP2102N-A02-GQFN20R
2 | U1202, U1203 | Fixed Positive LDO Regulator, 3.7V, 0.375V Dropout, PDSO6 | Texas Instruments | TLV70237DSET
2 | U1301, U1302 | IC SWITCH SPDTX4 4.5OHM 20LFCSP | Analog Devices | ADG1634BCPZ-REEL7
1 | Y100 | 48 MHz Â±10ppm Crystal 10pF 100 Ohms 4-SMD, No Lead | ECS Inc. | ECS-480-10-48-CKY-TR
2 | Y101, Y201 | CRYSTAL 32.7680KHZ 6PF SMD | Micro Crystal | CM8V-T1A-32.768KHZ-6PF-20PPM-TA-QC
1 | Y200 | 32 MHz Â±10ppm Crystal 10pF 100 Ohms 4-SMD, No Lead | ECS Inc. | ECS-320-10-48-CKY-TR

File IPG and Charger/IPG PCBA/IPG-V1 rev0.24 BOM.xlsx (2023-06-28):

Q-ty | Designator | Description | Manufacturer | Manufacturer PN
7 | C1, C2, R47, R48, R307, R308, R531 | Resistor, Zero ohms, 40V, 40mW, 1%, 0402, Imp-grd | Panasonic | ERJ-2GE0R00X
10 | C3, C15, C16, C26, C37, C45, C46, C92, C511, C514 | Capacitor, 4.7uF, X5R, 16V, 10%, 0603, Imp-grd | Murata | GRM188R61C475KE11
33 | C4-5, C7, C9, C11-14, C17, C27-33, C35-36, C38-39, C91, C93, C206-207, C243, C246-247, C301, C303-307 | Capacitor, 0.1uF, X7R, 16V, 10%, 0402, Imp-grd | Murata | GCM155R71C104KA55
3 | C6, C8, C507 | Capacitor, 470pF, X7R, 50V, 10%, 0402, Imp-grd | Murata | GCM155R71H471KA37D
6 | C10, C18, C19, C34, C95, C244 | Capacitor, 1.0uF, X5R, 16V, 10%, 0603, Imp-grd | Murata | GCM188R71C105KA64
5 | C20, C21, C505, C506, C510 | Capacitor, 4.7uF, X7S, 35V, 10%, 0805, Imp-grd | Murata | GCM21BC7YA475KE36L
8 | C22, C23, C24, C25, C87, C88, C89, C90 | Capacitor, 12pF, C0G, 25V, ±0.05pF, 0402, Imp-grd | AVX | C0402C120J3GACAUTO
2 | C94, C508 | Capacitor, 100pF, C0G, 50V, 5%, 0402, Imp-grd | Murata | GCM1555C1H101JA16D
1 | C96 | DNP: Capacitor, TBD, 0402, | TBD | TBD
1 | C97 | DNP: Capacitor, TBD, 0402 | TBD | TBD
1 | C98 | DNP, Capacitor, TBD .0402, | TBD | TBD
1 | C99 | Capacitor, DNP, 0402 | N/A | N/A
3 | C201, C241, C509 | Capacitor, 1000pF, X7R, 50V, 10%, 0402, Imp-grd | Murata | GRM1555C1H102JA01D
2 | C202, C205 | Capacitor, 0.33uF, X7S, 16V, 10%, 0402 | TDK | CGA2B1X7S1C334K050BC
1 | C203 | Capacitor, 1500pF, X7R, 50V, 10%, 0402 | Murata | GCM155R71H152KA37D
1 | C204 | Capacitor, 0.01uF, X7R, 50V, 10%, 0402, Imp-grd | Murata | GCM155R71H103KA55J
2 | C242, C245 | Capacitor, 2.2uF, X7R, 16V, 10%, 0603, Imp-grd | Murata | GRM188Z71C225ME43J
5 | C381, C382, C383, C384, C397 | Capacitor, 10uF, X5R, 50V, 10%, 0805 | Murata | GRM21BR61H106ME43L
16 | C401, C402, C403, C404, C405, C406, C407, C408, C409, C410, C411, C412, C413, C414, C415, C416 | Capacitor, 680pF, C0G, 100V, 5%, 0402 | TDK | C1005C0G2A681J050BE
3 | C501, C502, C504 | DNP: Capacitor, TBD, 0805 | TBD | TBD
1 | C503 | Capacitor, TBD, 0805 | TBD | TBD
2 | C512, C513 | Capacitor, 0.022uF, X7R, 50V, 10%, 0402, Imp-grd | Murata | GCM155R71H223KA55
11 | D1, D2, D3, D4, D5, D8, D9, D10, D502, D503, D508 | Schottky, 30V, 100mA, 385mV, 200mW, SOD-923 | ON Semi | NSR0130P2T5G
11 | D6, D7, D11, D12, D13, D14, D501, D504, D505, D506, D507 | Schottky, 40V, 500mA, 530mV, SOD-523 | ON Semi | NSR05T40XV2T5G
18 | D401-418 | TVS Diode, Bidirectional, ±9.5V, 4.5A, 0402 | TI | TPD1E10B09DPY
2 | F1, F2 | Fuse, 750mA, 63V, 1206 | Littelfuse | 0440.750WR
4 | J1, J2, J3, J4 | Kovar block, TBD | TBD | TBD
2 | J5, J6 | Coil TH pad, hole size and ring TBD | N/A | N/A
3 | J901, J902, J905 | Header, 1.27mm, male, 1x4, thru-hole | Samtec | TMS-104-01-G-S
2 | J907, J909 | Header, 1.27mm, male, 1x6, thru-hole | Samtec | TMS-106-01-G-S
2 | J910, J911 | Connector, 1.27 mm, 2x5, Male, TH | Samtec | FTSH-105-01-F-D-K
2 | L3, L501 | Inductor, 10uH, 600mA, 20%, 1008 | Wurth | 74438323100
1 | L5 | Inductor, 2.2uH, 1.76A, 1008 | TDK | VLS252010HBX-2R2M-1
1 | L6 | Inductor, Unshielded, 33nH, 350mA, 0402 | Murata | LQG15HS33NJ02D
2 | L97, L98 | Inductor, TBD, 0402 | TBD | TBD
1 | L99 | Inductor, DNP, 0402 | N/A | N/A
10 | M1, M2, M5, M13, M21, M22, M24, M27, M28, M30 | MOSFET, P-chan, -20V, X2-DFN1006-3 | Diodes Inc | DMP21D5UFB4-7B
18 | M3, M4, M6, M7, M8, M11, M12, M14, M15, M16, M19, M20, M23, M25, M26, M29, M31, M319 | MOSFET, N-Chan, 20V, DFN0606 | Diodes Inc | DMN2990UFZ
5 | M9, M10, M17, M18, M506 | MOSFET, P-chan, -20V, DFN1010-3 | Diodes Inc | DMP2043UCA3-7
5 | M32, M504, M507, M508, M510 | MOSFET, P-chan, -50V, DFN1006 | Diodes Inc | DMP58D0LFB
3 | M33, M91, M318 | MOSFET, P-chan, -20V, DFN0604 | Diodes Inc | DMP22D4UFO
5 | M34, M501, M502, M503, M505 | MOSFET, N-Chan, 60V, 320mA, DFN1006 | Diodes Inc | DMN62D1LFB-7B
5 | M301, M302, M303, M304, M317 | MOSFET, N-Chan, 60V, DFN1006 | Diodes Inc | DMN65D8LFB-7B
5 | M509, M511, M512, M513, M514 | MOSFET, N-Chan, 60V, DFN1006 | Diodes Inc | DMN62D1SFB
1 | M515 | MOSFET, N-Chan, 20V, DFN1006 | Diodes Inc | DMN2501UFB4
5 | Q301, Q302, Q303, Q304, Q317 | TRANS 2PNP 40V 0.2A SOT963 | ON Semi | NST3906DP6T5G
6 | Q318, Q321, Q322, Q323, Q324, Q337 | Transistor, NPN, 45V, 100mA, DFN1006 | Diodes Inc | BC847BLP-7B
1 | R1 | Resistor, 10.0M,1%, 0402, Imp-grd | Panasonic | ERJ-2GEJ106X
10 | R2, R4, R13, R15, R40, R42, R43, R201, R202, R367 | Resistor, 10.0M,, 1%, 0402, Imp-grd | Panasonic | ERJ-2GEJ106X
2 | R3, R33 | Resistor, 5.10M, 5%, 0402, Imp-grd | Panasonic | ERJ-2GEJ515X
4 | R5, R34, R52, R53 | Resistor, 10.0k, 1%, 0402, Imp-grd | Panasonic | ERJ-2RKF1002X
19 | R6, R21, R37, R41, R207-208, R213-214, R241-242, R247-248, R253-254, R309, R351-354 | Resistor, 10.0M, 1%, 0402, Imp-grd | Panasonic | ERJ-2GEJ106X
1 | R7 | Resistor, 10.0M, 40V, 40mW, 1%, 0402, Imp-grd | Panasonic | ERJ-2GEJ106X
2 | R8, R16 | Resistor, 4.02k, 1%, 0402, Imp-grd | Panasonic | ERJ-2RKF4021X
1 | R9 | Resistor, 7.50k, , 1%, 0402, Imp-grd | Panasonic | ERJ-2RKF7501X
2 | R10, R18 | Resistor, 619k, 0.1%, 0402 | Vishay | MCS0402MD6193BE000
1 | R11 | Resistor, 243k,, 0.1%, 0402 | TE Connectivity | RP73PF1E243KBTDF
24 | R12,R14,R20,R22-24,R26,R27,R29,R209,R212,R250,R252,R502-504,R507,R509-510,R512,R514-515,R519,R526 | Resistor, 1.00M, 1%, 0402, Imp-grd | Panasonic | ERJ-2RKF1004X
1 | R17 | Resistor, 7.50k, 1%, 0402, Imp-grd | Panasonic | ERJ-2RKF7501X
1 | R19 | Resistor, 243k, 0.1%, 0402 | TE Connectivity | RP73PF1E243KBTDF
6 | R25, R28, R371, R372, R374, R387 | Resistor, 2.00M, 1%, 0402, Imp-grd | Panasonic | ERJ-2GEJ205X
3 | R30, R255, R300 | Resistor, Zero ohms, 1%, 0402, Imp-grd | Panasonic | ERJ-2GE0R00X
13 | R31, R49, R50, R281, R282, R283, R284, R297, R299, R524, R527, R529, R530 | Resistor, DNP, 0402 | N/A | N/A
1 | R32 | Resistor, 1.00M 1%, 0402, Imp-grd | Panasonic | ERJ-2RKF1004X
1 | R35 | Resistor, 100,, 1%, 0402, Imp-grd | Panasonic | ERJ-2RKF1000X
1 | R36 | Resistor, 10.0M, 1% 0402, Imp-grd | Panasonic | ERJ-2GEJ106X
1 | R38 | Resistor, 340k, 1%, 0402, Imp-grd | Panasonic | ERJ-2RKF3403X
1 | R39 | Resistor, 40.2k, 1%0402, Imp-grd | Panasonic | ERJ-2RKF4022X
2 | R44, R516 | Resistor, 150k, 1%, 0402, Imp-grd | Panasonic | ERJ-2RKF1503X
2 | R45, R46 | Resistor, 49.9k, 1%, 0402, Imp-grd | Panasonic | ERJ-2RKF4992X
3 | R51, R54, R55 | Resistor, 10.0k, 40V, 40mW, 1%, 0402, Imp-grd | Panasonic | ERJ-2RKF1002X
1 | R203 | Resistor, 180k,1%, 0402 | KOA Speer | RK73H1ETTP1803F
1 | R204 | Resistor, 180k,, 1%, 0402 | KOA Speer | RK73H1ETTP1803F
1 | R205 | Resistor, 360k,, 1%, 0402, Imp-grd | Panasonic | ERJ-2RKF3603X
1 | R206 | Resistor, 1.40M, 1%, 0402, Imp-grd | Yageo | RC0402FR-071M4L
2 | R210, R506 | Resistor, 1.00M, 1%, 0402, Imp-grd | Panasonic | ERJ-2RKF1004X
1 | R211 | Resistor, 249k, 1%, 0402, Imp-grd | Panasonic | ERJ-2RKF2493X
1 | R215 | Resistor, Zero ohms,1%, 0402, Imp-grd | Panasonic | ERJ-2GE0R00X
1 | R243 | Resistor, 180k, 1%, 0402 | KOA Speer | RK73H1ETTP1803F
1 | R244 | Resistor, 180k, 1% 0402 | KOA Speer | RK73H1ETTP1803F
1 | R245 | Resistor, 360k, 1%, 0402, Imp-grd | Panasonic | ERJ-2RKF3603X
1 | R246 | Resistor, 1.40M, 40V, 40mW, 1%, 0402, Imp-grd | Yageo | RC0402FR-071M4L
5 | R249, R517, R518, R521, R525 | Resistor, 1.00M,, 1%, 0402, Imp-grd | Panasonic | ERJ-2RKF1004X
1 | R251 | Resistor, 100k, 1% 0402, Imp-grd | Panasonic | ERJ-2RKF1003X
2 | R276, R279 | Resistor, 1.00M, 40V, 40mW, 1%, 0402, Imp-grd | Panasonic | ERJ-2RKF1004X
1 | R277 | Resistor, 100 ohms, 1%, 50V, 0.1W, 0402 | Panasonic | ERJ-2RKF1000X
6 | R278, R311, R312, R313, R314, R327 | Resistor, 1.00k, 1%, 50V, 0.1W, 0402 | Panasonic | ERJ-2RKF1001X
1 | R298 | Resistor, 10.0k,, 1%, 0402, Imp-grd | Panasonic | ERJ-2RKF1002X
4 | R301, R302, R305, R306 | DNP: Resistor, TBD, 0402 | TBD | TBD
2 | R303, R304 | Resistor, 100k, 40V, 40mW, 1%, 0402, Imp-grd | Panasonic | ERJ-2RKF1003X
5 | R331, R332, R333, R334, R347 | Resistor, 40.2 ohms, 50V, 100mW, 1%, 0402 | Panasonic | ERJ-2RKF40R2X
1 | R373 | Resistor, 2.00M,, 1%, 0402, Imp-grd | Panasonic | ERJ-2GEJ205X
1 | R501 | Resistor, 402 ohms, 1%, 0402, Imp-grd | Panasonic | ERJ-2RKF4020X
1 | R505 | RES SMD 49.9 OHM 1% 1/8W 0805 | Panasonic | ERJ-6ENF49R9V
2 | R508, R522 | Resistor, 100k, 1%, 0402, Imp-grd | Panasonic | ERJ-2RKF1003X
2 | R511, R528 | Resistor, 402 ohms, 1%, 0402, Imp-grd | Panasonic | ERJ-2RKF4020X
1 | R513 | Resistor, 1.00M, 1% 0402, Imp-grd | Panasonic | ERJ-2RKF1004X
1 | R520 | Resistor, 40.2k, 1%, 0402, Imp-grd | Panasonic | ERJ-2RKF4022X
1 | R523 | Resistor, 2.00M,1%, 0402, Imp-grd | Panasonic | ERJ-2GEJ205X
1 | SW901 | Pushbutton, NO-MOM, 12V, 0.05A, SMT | C&K | PTS647SN50SMTR2LFS
3 | U1, U10, U11 | LDO Regulator, 3.3V, Shutdown, DFN1010-4 | Diodes Inc | AP7354D-33FS4-7
2 | U2, U4 | Charge Controller, 4.2V, 250mA, DFN-6 | Linear | LTC4065LEDC#TRMPBF
2 | U3, U5 | Comparator, 1.2V Reference, Open-drain, BGA-4 | TI | TLV4021R1YKAR
6 | U6, U7, U14, U15, U16, U501 | Op Amp, Rail-to-Rail, 95kHz, WLCSP-6 | Analog Devices | AD8505ACBZ
1 | U8 | Magnet Sensor, 15 Gauss, ULLGA4, Imp-grd | NVE | ADL021-14E
1 | U9 | FRAM, 8 Mbit (1024k x 8), SPI, 1.8-3.6V, QFN-8 | Cypress Semi | CY15B108QN-20LPXC
1 | U12 | SEPIC 1.23V 1 Output 75mA (Switch) SOT-23-5 | Linear | LT1615ES5-1#TRPBF
1 | U13 | Digital potentiometer, 256 taps, 100k, I2C, QFN-10 | Renesas | ISL23315TFRUZ-T
1 | U17 | MCU, ARM Cortex-M33, 2 MB, 786 kB RAM, BGA-132 | STMicro | STM32U585QII3
1 | U18 | Reset Monitor, 2.63V, Active low, X2SON | TI | TPS3831L30
2 | U30, U31 | IC SWITCH SPDTX4 4.5OHM 20LFCSP | Analog Devices | ADG1634BCPZ-REEL7
1 | U91 | Bluetooth, v5.0, 192 kB Flash, 24 kB RAM, BGA-33 | Nordic | NRF52810-CAAA
2 | U201, U203 | Analog front end, ECG, RLD amp, BGA-20 | Analog Devices | AD8233ACBZ
1 | U301 | DAC, 16-bit, Dual channel, SPI/I2C, WSON-10 | TI | DAC80502DRXT
2 | U303, U304 | Analog Switch, SPDT, 2:1, DSBGA6 | TI | TS5A3159AYZPR
2 | U305, U310 | Op Amp, Dual, Rail-to-Rail, 1MHz, BGA-9 | TI | TLV9002SIYCKR
1 | U306 | Monostable, RC set, dual triggers, BGA-8 | TI | SN74LVC1G123YZPR
1 | U307 | AND gate, Dual 2-input, BGA-8 | TI | SN74LVC2G08YZPR
2 | U308, U309 | Multiplexer, 8:1, 0.7 ohms, QFN-16 | Maxim | MAX4781ETE+T
1 | U311 | Differential Amplifier, 110 MHz, DFN-8 | Analog Devices | AD8137YCPZ
1 | U502 | Comparator, Push-pull output, SC-70 | TI | TLV3691IDCKT
1 | U503 | Buck-Boost Converter, Selectable Voltage, QFN-20 | Analog Devices | LTC3130IUDC-1#PBF
2 | Y1, Y91 | Crystal, 32.768kHz, 6.0pF, 70k, CC8V, Imp-grd | Micro Crystal AG | CM8V-T1A-32.768KHZ-6PF-20PPM-TA-QC
1 | Y92 | Imp-grd Crystal 32 MHz 10pF 100 Ohms 4-SMD | ECS | ECS-320-10-48-CKY-TR
1 | Y2 | Crystal, 48 MHz Crystal 10pF 100 Ohms 4-SMD | ECS | ECS-480-10-48-CKY-TR

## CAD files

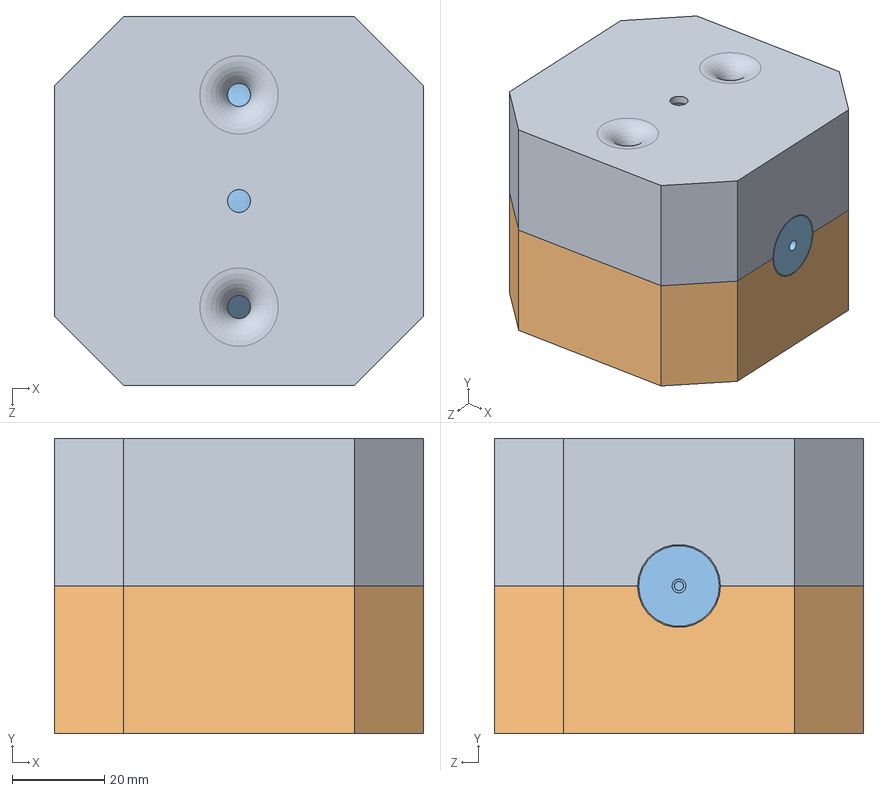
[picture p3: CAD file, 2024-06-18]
Physical Sensors/Bladder Ellipsoid_mold_v1/Ellipsoid_mold_v1.SLDASM
80.0 x 64.0 x 80.0 mm
sphere_mold_bottom_ellipsoidV2
ellipsoid v1
Ellipsoid_mold_top

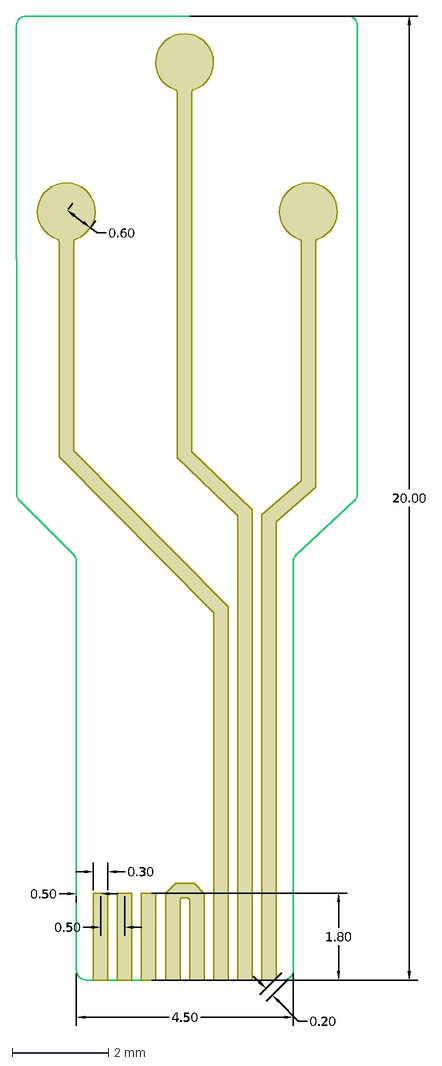
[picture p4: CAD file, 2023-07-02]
Chemical Sensors/Thin Film Electrode Design/HORNET_1v0.3 PIEFclean.dxf
0.50
0.30
4.50
0.20
20.00
1.80
0.60

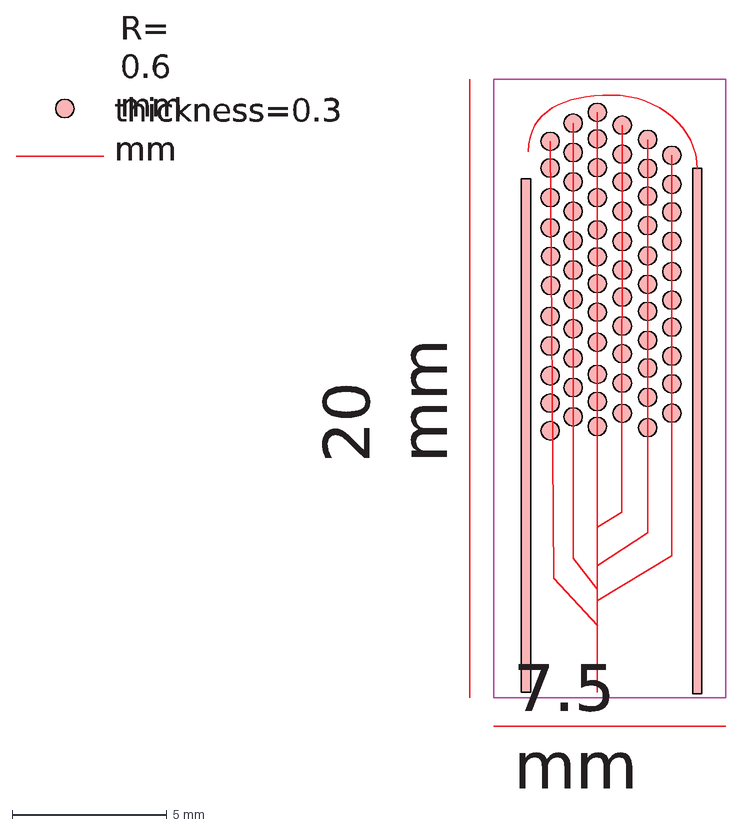
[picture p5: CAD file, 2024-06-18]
Chemical Sensors/Y2-NEST5-Echem Sensor-Data Analysis.dxf
7.5 mm
20 mm
R= 0.6 mm
thickness=0.3 mm

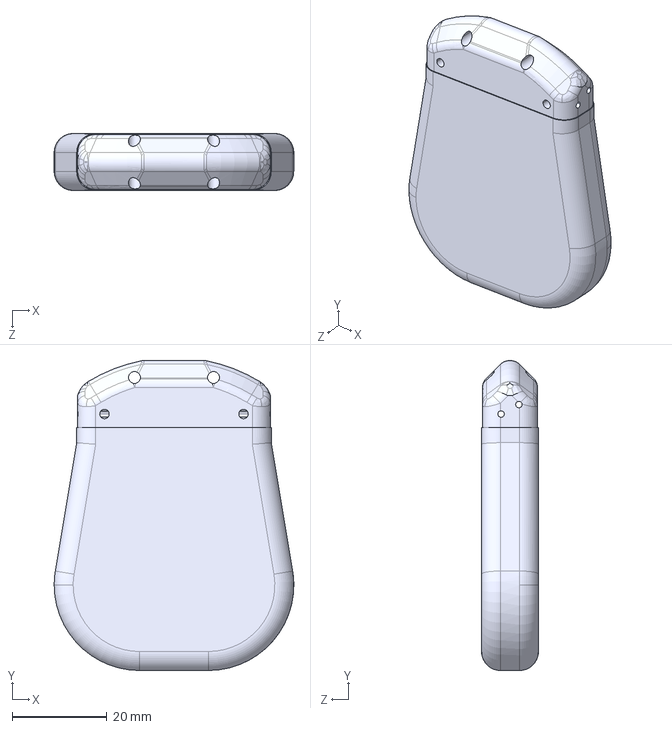
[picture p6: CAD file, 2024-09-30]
IPG and Charger/Mechanical Design - IPG and Charger/12mm IPG model.STEP
50.5 x 65.3 x 12.0 mm

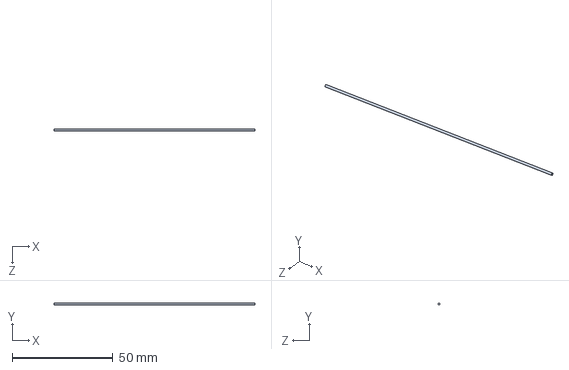
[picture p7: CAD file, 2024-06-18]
Parylene Cuff Electrode/Design/SLDPRT Files/Nerve.SLDPRT
100.0 x 0.9 x 0.9 mm

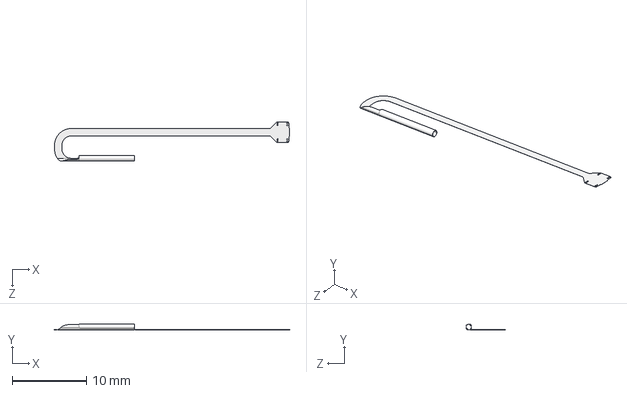
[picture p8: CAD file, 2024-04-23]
Parylene Cuff Electrode/Design/STEP Files/E3- Large.STEP
31.6 x 0.759 x 5.29 mm

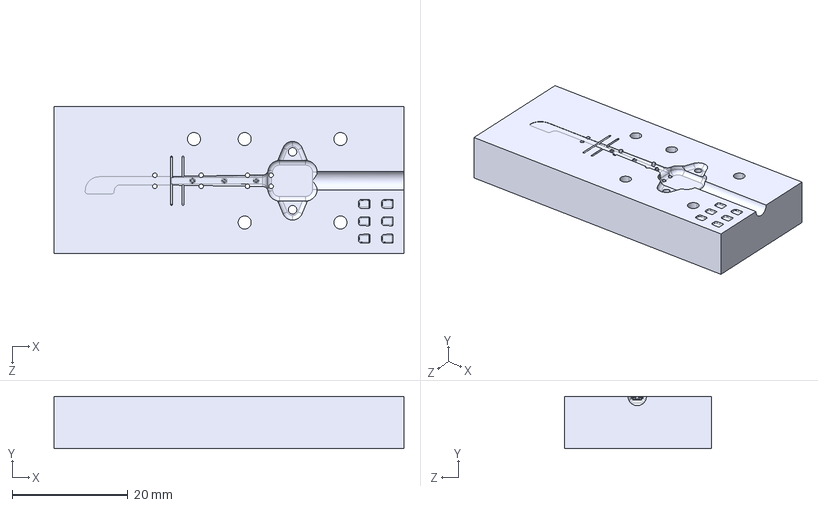
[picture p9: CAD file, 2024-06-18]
Parylene Cuff Electrode/Fabrication and Packaging/Overmold STEP and Solidworks Models (Rev 1)/OvermoldBase_v1.STEP
60.5 x 9.00 x 25.4 mm

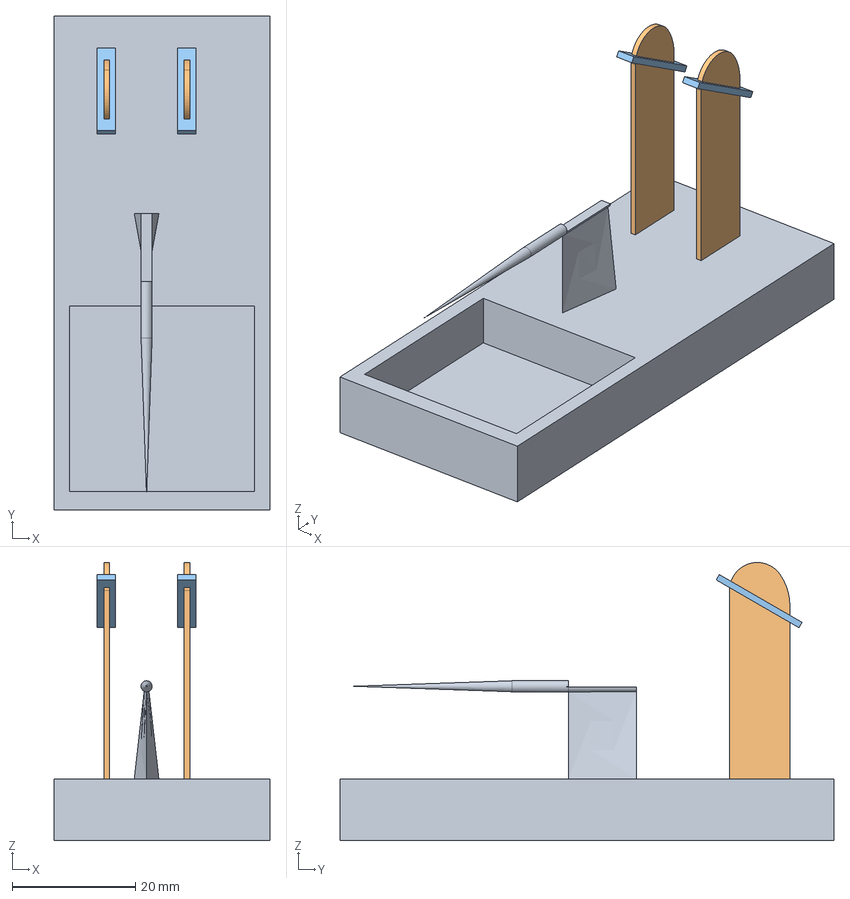
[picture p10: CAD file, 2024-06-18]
Parylene Cuff Electrode/Surgical Placement Tool/Placement tool-expander tool.step
35.0 x 80.0 x 45.1 mm

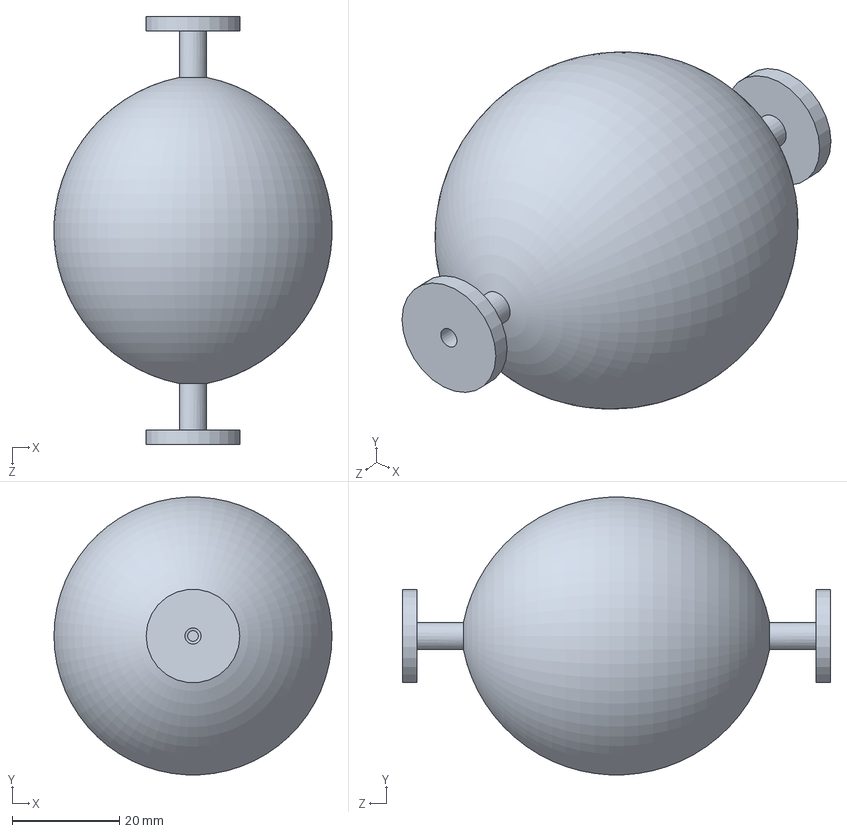
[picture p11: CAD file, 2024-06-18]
Physical Sensors/Bladder Ellipsoid_mold_v1/ellipsoid v1.SLDPRT
51.9 x 51.9 x 80.0 mm

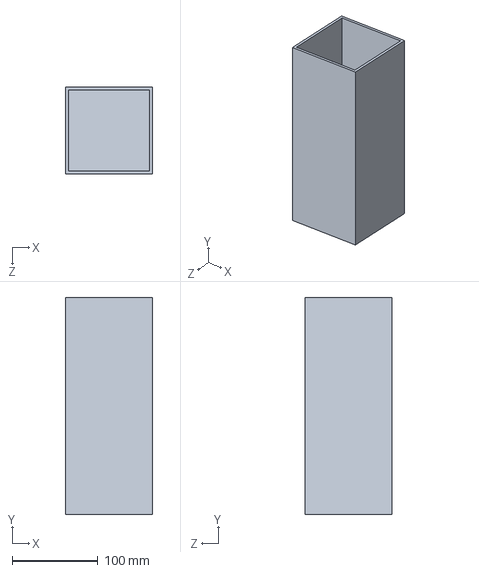
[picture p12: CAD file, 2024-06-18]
Physical Sensors/Strain Sensor/Strain Sensor Thermal accelerated aging setup design 3/Acrylic rectangular tank.SLDPRT
101.5 x 253.6 x 101.5 mm

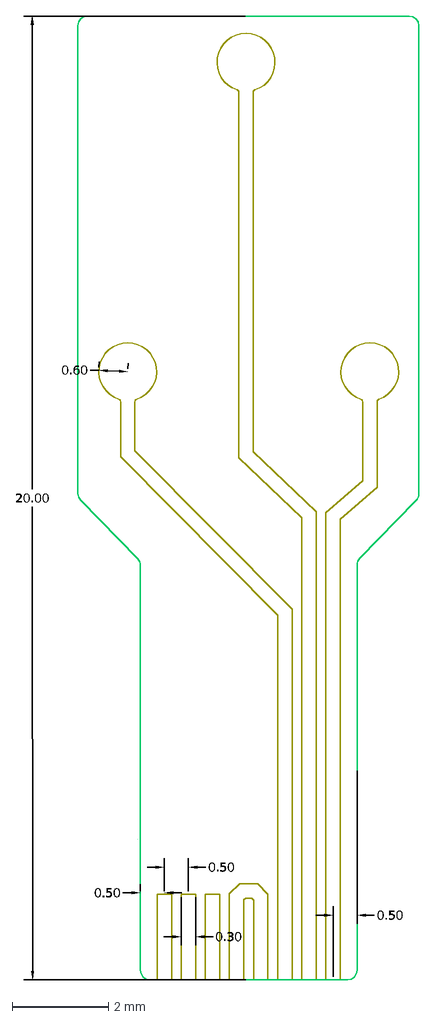
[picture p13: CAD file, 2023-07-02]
Chemical Sensors/Thin Film Electrode Design/HORNET_2v0.3 PIEFClean.dxf
0.60
0.50
0.30
20.00

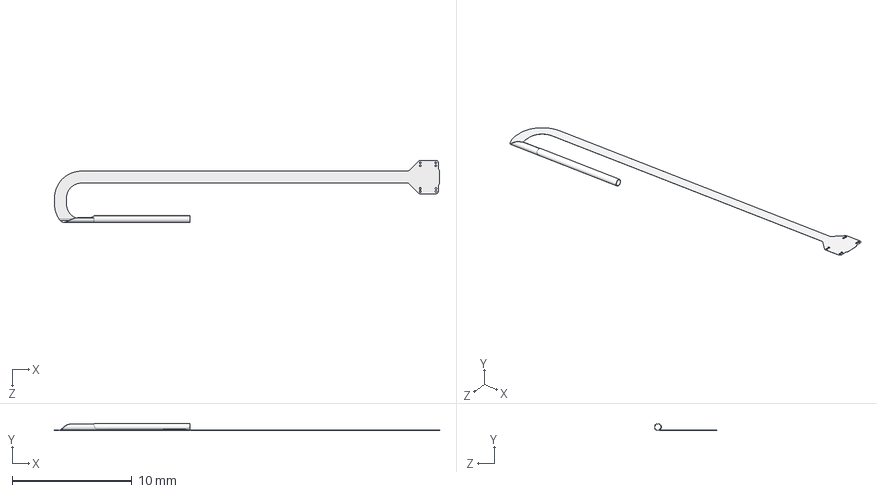
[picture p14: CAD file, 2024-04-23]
Parylene Cuff Electrode/Design/STEP Files/E3- Small.STEP
32.1 x 0.574 x 5.20 mm

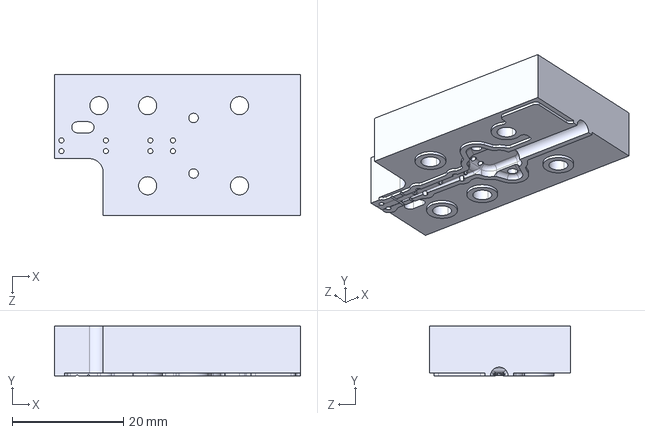
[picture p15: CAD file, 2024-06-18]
Parylene Cuff Electrode/Fabrication and Packaging/Overmold STEP and Solidworks Models (Rev 1)/OvermoldTop_v1.STEP
44.3 x 9.00 x 25.4 mm

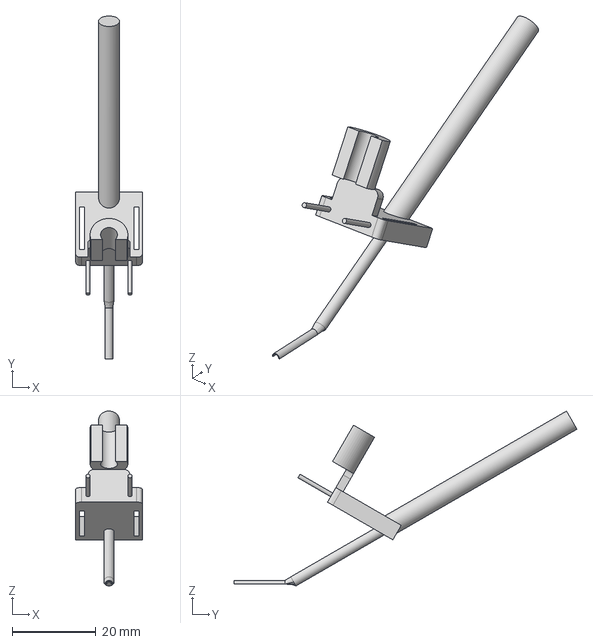
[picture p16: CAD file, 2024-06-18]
Parylene Cuff Electrode/Surgical Placement Tool/Placement tool.step
16.0 x 81.8 x 41.7 mm

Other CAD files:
Physical Sensors/Strain Sensor/NEST 5 Strain Sensor Mask CAD File.dwg
Physical Sensors/Temperature Sensor/Nest 5-Temp sensor mask design.dwg
Physical Sensors/Bladder Ellipsoid_mold_v1/Ellipsoid_mold_top.SLDPRT
Physical Sensors/Strain Sensor/Strain Sensor Thermal accelerated aging setup design 3/HeaterV3_SensorBotClamp_V2.SLDPRT
IPG and Charger/Mechanical Design - IPG and Charger/12mm IPG model.STL
Parylene Cuff Electrode/Design/SLDPRT Files/Archived/B3- Large.SLDPRT
Parylene Cuff Electrode/Design/SLDPRT Files/Archived/E3- Large.SLDPRT
Parylene Cuff Electrode/Design/SLDPRT Files/Archived/E3- Small.SLDPRT
Parylene Cuff Electrode/Design/SLDPRT Files/B3- Large.SLDPRT
Parylene Cuff Electrode/Design/SLDPRT Files/E3- Large.SLDPRT
Parylene Cuff Electrode/Design/SLDPRT Files/E3- Small.SLDPRT
Parylene Cuff Electrode/Design/STEP Files/Archived/B3- Large.STEP
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

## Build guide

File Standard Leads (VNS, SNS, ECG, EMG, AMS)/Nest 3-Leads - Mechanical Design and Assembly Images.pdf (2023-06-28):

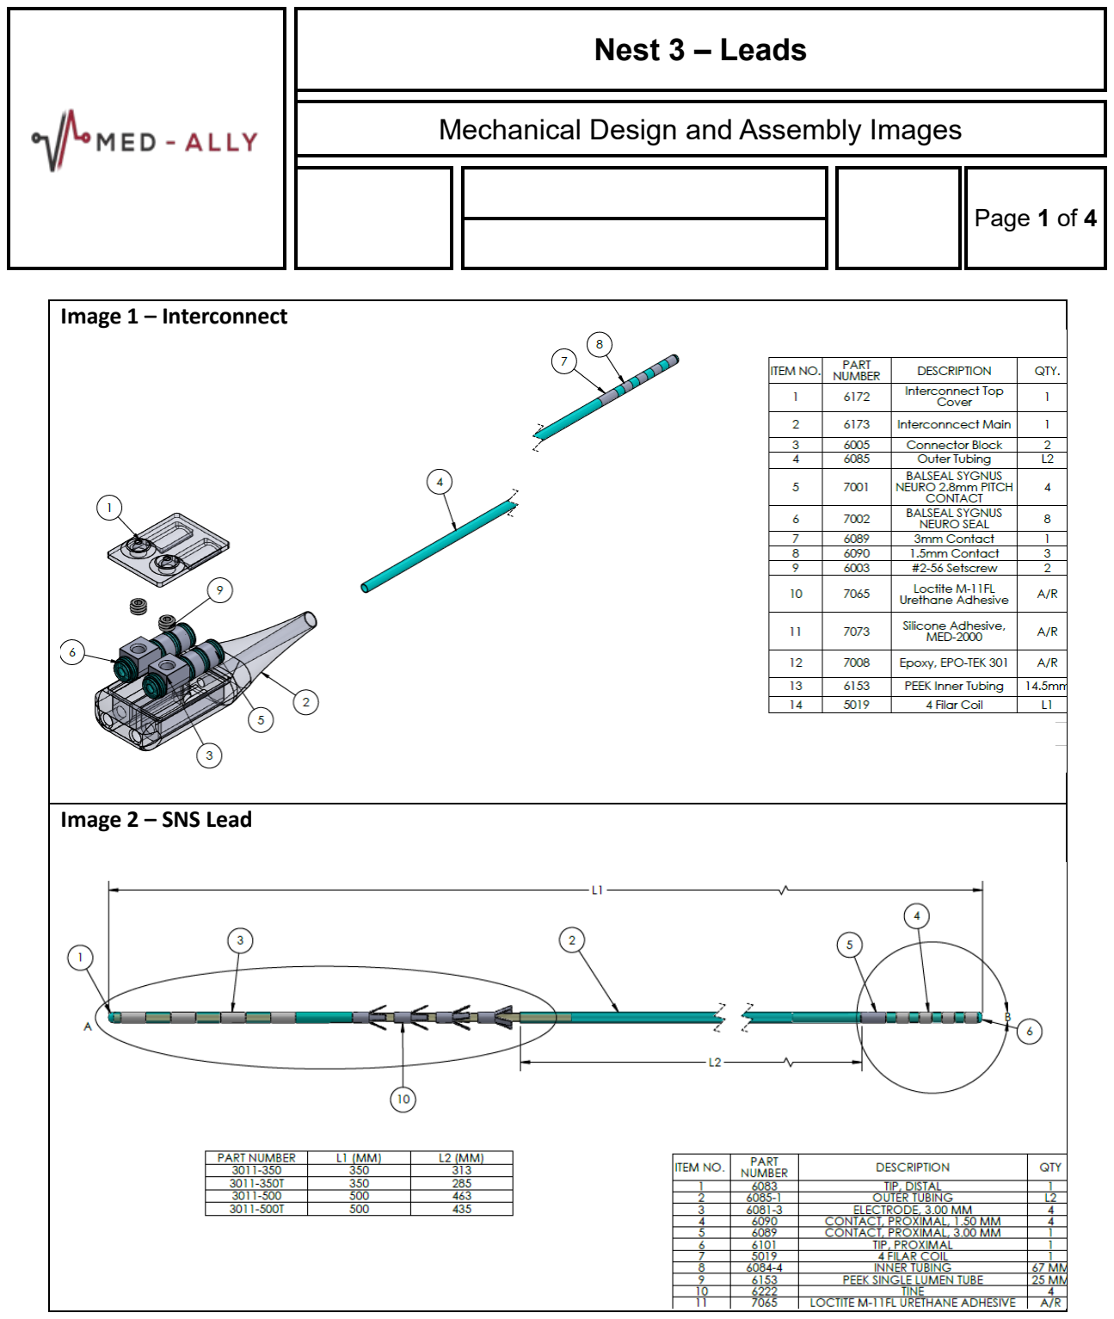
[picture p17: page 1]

Nest 3 – Leads

Mechanical Design and Assembly Images

Page 1 of 4

Image 1 – Interconnect

Image 2 – SNS Lead

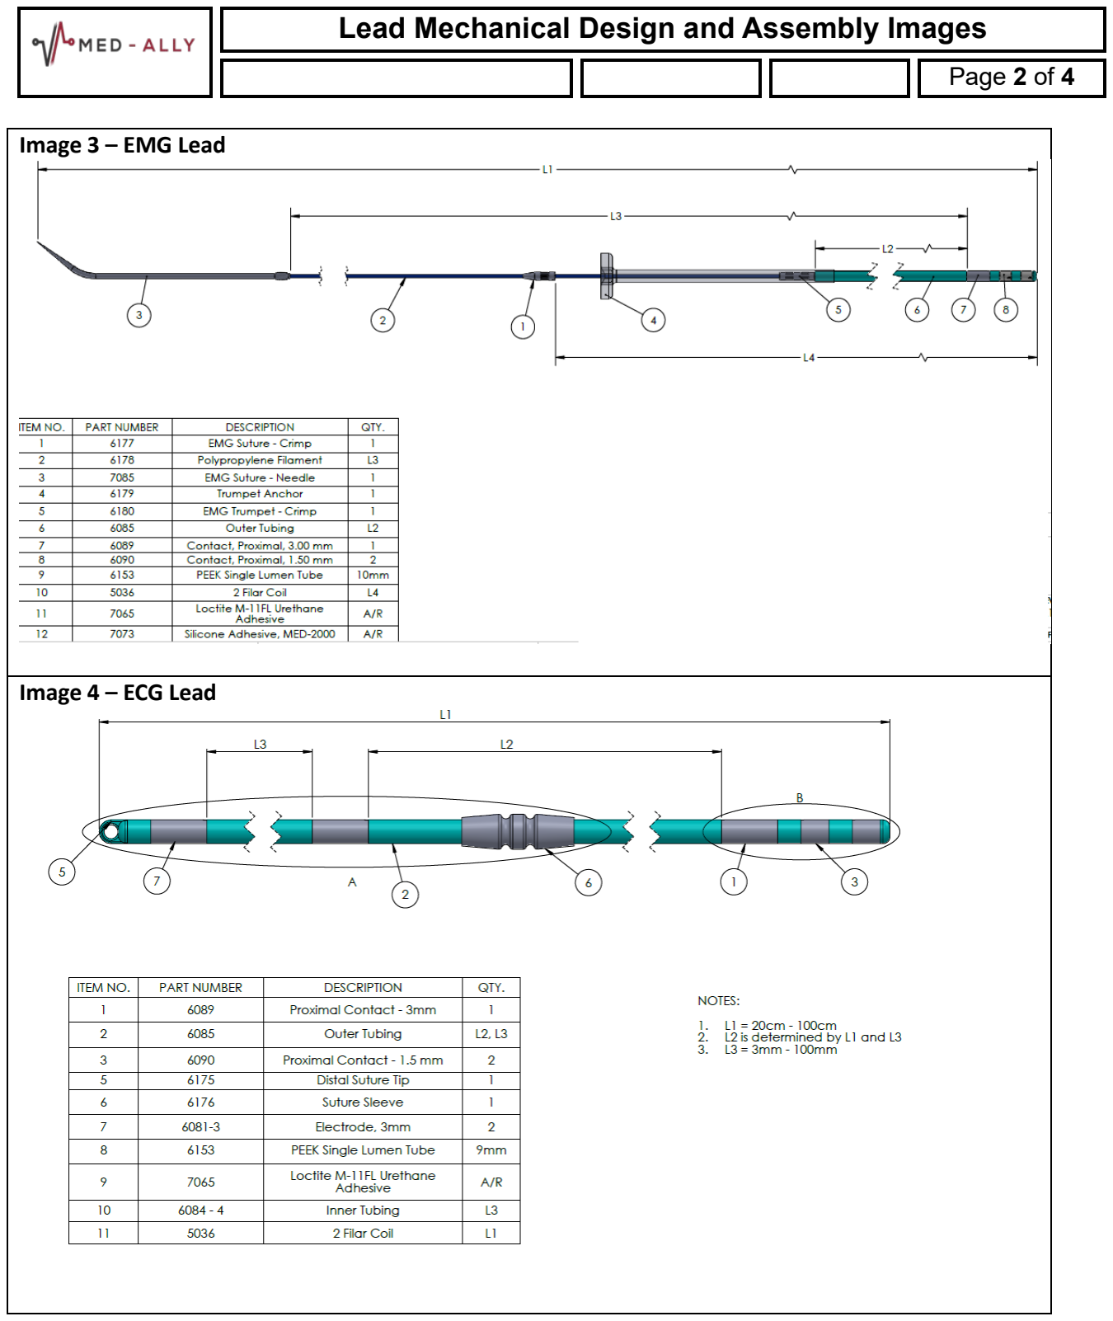
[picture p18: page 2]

Lead Mechanical Design and Assembly Images
Page 2 of 4

Image 3 – EMG Lead

Image 4 – ECG Lead

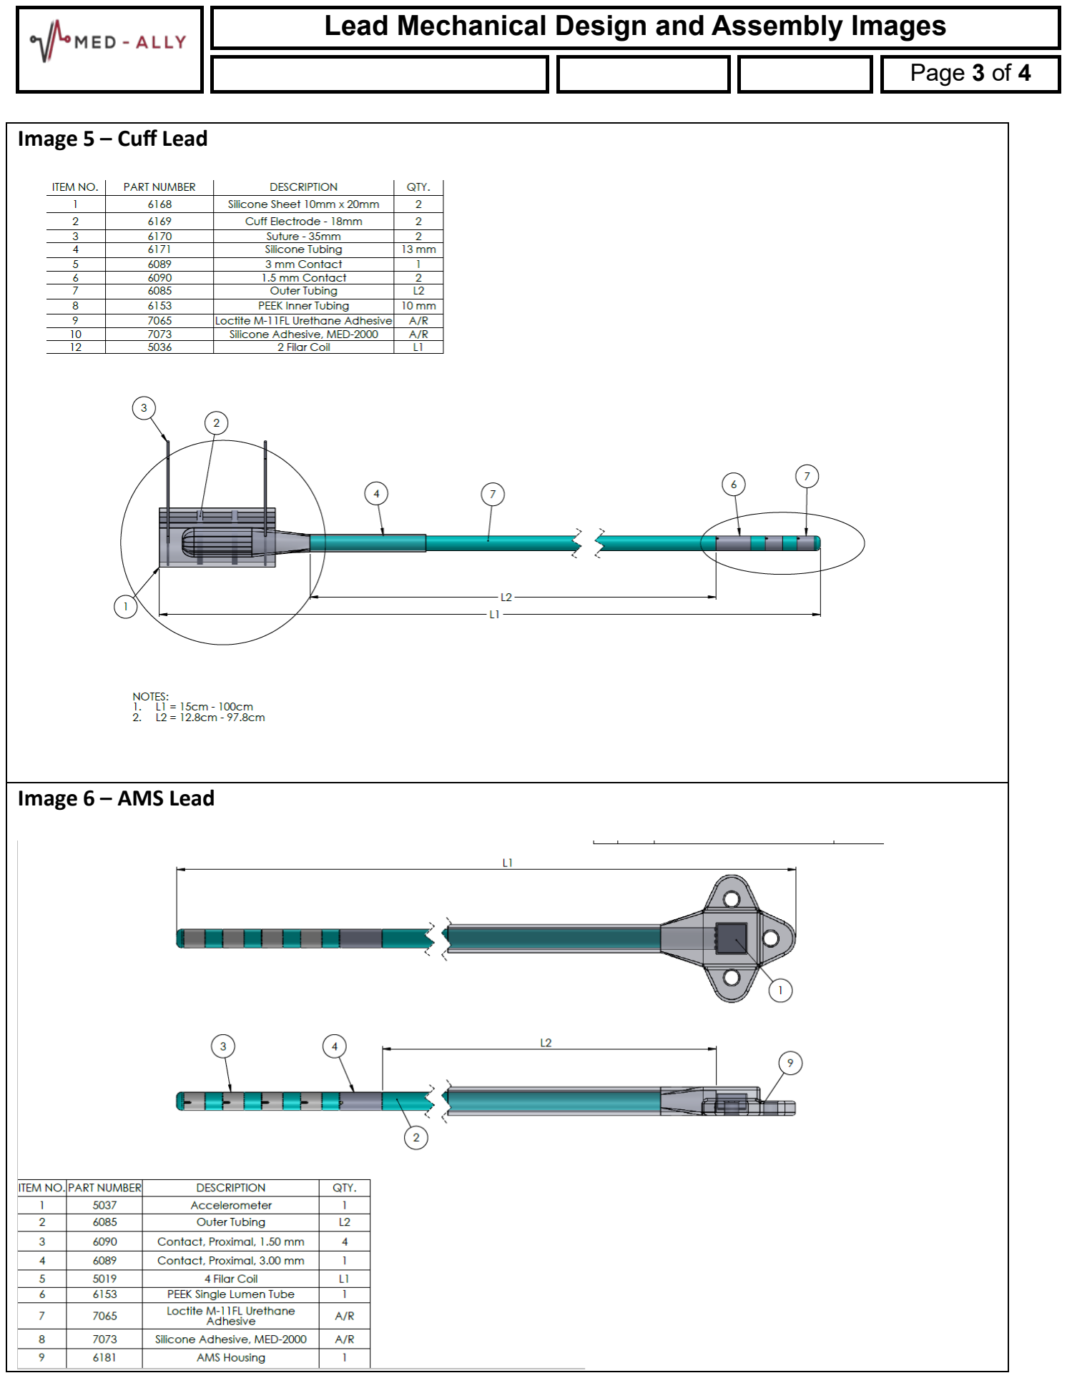
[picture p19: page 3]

Page 3 of 4

Image 5 – Cuff Lead

Image 6 – AMS Lead

Page 4 of 4

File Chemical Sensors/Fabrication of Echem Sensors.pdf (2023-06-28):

# NEST 5 – Fabrication Protocol

Revision 1 (15 June 2023)

## 1. Electrode Design

The electrodes were designed using easyEDA software and were fabricated on a thin parylene C film as shown below. The electrodes are in a module that is 20 mm x 7 mm (20 µm thick) with conductive Pt leads (200 nm thick), and electrodes diameter of 1.2 mm. The distance between the leads are chosen in order to be compatible with the Zero Insertion Force (ZIF) connectors to facilitate the testing process.

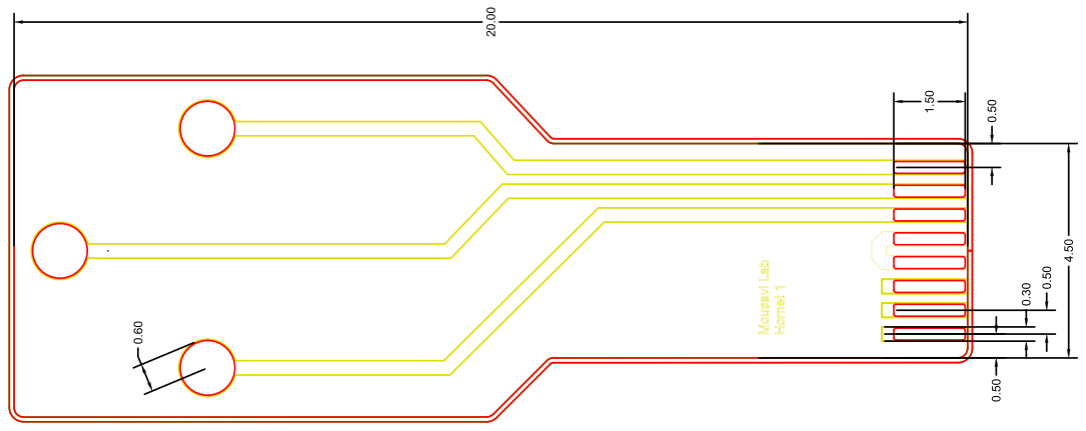
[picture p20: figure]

Figure 1.1. Schematic of the electrochemical sensor.

## 2. Parylene Electrode Fabrication

The electrodes were fabricated according to the protocol developed by Meng and Scholten, reported in the PIE foundry (https://piefoundry.usc.edu/). Below is the detailed fabrication protocol.

### 2.1. Base parylene C Layer

1. Wafers
- <100> Si wafer
- 500 um thick
- 100 mm diameter
- Double-side-polished

2. Dry-bake
- Dry-bake the wafers in an oven at 110 C (or higher) for at least 15 minutes;
- Or on a hotplate at a similar temperature for at least 3 minutes.
- Tool: Cascade Tek or Lindberg Blue vacuum oven
3. Parylene C Deposition
- Deposit a 10 micron thick layer of Parylene C on to wafers using Parylene C deposition protocol on section 4.1.
4. Thermal Anneal
- Vacuum anneal Parylene C coated wafers
- Time: 4 hour
- Temperature: 150 C
- Pressure: Full vacuum
- Tool: Cascade Tek oven
5. Oxygen Plasma
- Expose wafers to oxygen plasma
- Time: 300 seconds
- Temperature: Room temperature
- Pressure: 125 mTorr
- Power: 100 W
- Flow: 30 SCCM O2
- Tool: YES Asher

### 2.2. Electrode Layer

6. Image Reversal Lithography
- Prepare an image reversal photoresist mask of the electrodes, traces and contact pads, using the protocol on section 4.2.
- Confirm thickness of photoresist with profilometer. Target is 1.1± 0.1 micron.
7. Oxygen Plasma
- Expose wafers to oxygen plasma
- Time: 300 seconds
- Temperature: Room temperature
- Pressure: 125 mTorr
- Power: 100 W
- Flow: 30 SCCM O2
- Tool: YES Asher
8. Metal Deposition
- Evaporate a 200 nm thick Pt metal layer.
- Tool: CHA Mark 50 Evaporator
9. Lift-Off
- Lift-off excess metals to define the pattern using the protocol on section 4.3.

### 2.3. Insulation of Parylene C Layer

10. Oxygen Plasma

- Expose wafers to oxygen plasma
- Time: 300 seconds
- Temperature: Room temperature
- Pressure: 125 mTorr
- Power: 100 W
- Flow: 30 SCCM O2
- Tool: YES Asher
11. Silanization
- Silanize Pt surface of metal layer prior to insulation coating using the protocol on section 4.4.
12. Parylene C Deposition
- Deposit a 10 micron thick layer of Parylene C on to wafers using the Protocol on section 4.1.
13. Thermal anneal
- Vacuum anneal Parylene C coated wafers
- Time: 4 hour
- Temperature: 150 C
- Pressure: Full vacuum
- Tool: Cascade Tek oven

### 2.4. Parylene Etch #1

14. Etch Mask
- Prepare a photoresist etch mask, approx. 15 um thick, defining the outline of the MEA using the protocol on section 4.5.
15. RIE Etch
- Etch approximately 10 microns of Parylene C using O RIE. Etch depth should
2
match the first Parylene C layer thickness.
- Time: Approximately 60 minutes
- Temperature: Room temperature
- Pressure: 150 mTorr
- Power: 150 W
- Flow: 50 SCCM O2
- Tool: Oxford RIE 80
- Current estimated etch rate: 0.185 micron/minute (1 wafer); 0.165 micron/minute (2 wafer)
16. Strip Mask
- Strip photoresist mask in sequential baths of acetone (2-5 minutes), isopropanol (2-5 minutes), and rinse 3x in DI water.
- Blow dry with nitrogen
17. Dry Bake
- Dry bake wafers under partial vacuum and nitrogen flow
- Time: > 15 minutes
- Temperature: 60 C

- Pressure: 15" Hg
- Flow: 15 SCCM nitrogen
- Tool: Cascade Tek or Lindberg Blue vacuum oven

### 2.4. Parylene Etch #2

18. Etch Mask
- Prepare a photoresist etch mask, approx. 15 um thick, defining the outline of the MEA, and the openings over the electrodes and contact pads using the protocol on section 4.5.
19.RIE Etch
- Etch approximately 10 microns of Parylene C using O2 RIE. Etch depth should match second Parylene C layer thickness.
- Time: Approx. 60 minutes
- Temperature: Room temperature
- Pressure: 150 mTorr
- Power: 150 W
- Flow: 50 SCCM O2
- Tool: Oxford RIE 80
- Current estimated etch rate: 0.185 micron/minute (1 wafer); 0.165 micron/minute (2 wafer)
20.Strip Mask
- Strip photoresist mask in sequential baths of acetone (2-5 minutes), isopropanol (2-5 minutes), soak in DI water
21.Release MEAs
- Slowly peel MEAs off wafer while submerged in water using tweezers.

### 2.4. Post-Processing

22. Thermal Anneal
- Vacuum anneal MEAs sandwiched between ceramic plates.
- Purge oven 3x with nitrogen prior to starting program
- Time: 48 hour; 8 hour ramp up; 8 hour ramp down
- Temperature: 200 C;
- Pressure: Full vacuum
- Tool: Cascade Tek
23. High-Temperature Anneal
- Install Dataplate hotplate in Cascade Tek vacuum oven using rubber feedthrough and wire terminal block.
- Seal leaks around feedthrough using Parafilm.
- Place devices sandwiched between ceramic plates on hotplate
- Set temperature to 275 with 180 C per hour ramp
- Pump down oven, then close vacuum and flood with nitrogen at 25-50 sccm

- Ramp for 1.5 hour, then bake for an additional 3 hours; Unplug the hotplate and let cool below 90 C.
- Time: 3 hour bake; 1.5 hour ramp up; 1-2 hour cool down.
- Temperature: 275 C;
- Pressure: Atmosphere
- Flow: 25-30 SCCM nitrogen
- Tool: Cascade Tek oven and Dataplate hotplate
24. Oxygen Plasma
- Attach MEAs to carrier wafer (Si or glass) face-up, using small bits of kapton tape.
- Time: 300 seconds
- Temperature: Room temperature
- Pressure: 125 mTorr
- Power: 100 W
- Flow: 30 SCCM O2
- Tool: YES Asher

## 3. Packaging

1. Cut the PEEK (250 micron thickness, from McMaster) with a size more than the electrode connector side.
2. Attach the connector section of the electrodes to the backing PEEK using small strips of polyimide tape
3. Permanently adhere the electrode to the PEEK using Epotek 301 epoxy.
- Mix the epoxy.
- Put two small drops on both side of the electrode to diffuse between the Parylene and PEEK
4. Place the electrodes under vacuum using a bell jar to remove air bubbles
5. Cure the epoxy in an oven at 55 C for 1.5 hours.
6. Remove the polyimide tape
7. Cut the PEEK from edges of the electrodes using an exact knife and/or microscissors.

## 4. Protocols

### 4.1. Parylene C chemical Vapor Deposition

- Warnings
Items not allowed in chamber: wood, scotch tape, liquids, anything capable of off-gassing.

- Parameters for Parylene C:
- Vaporizer heater: 175 °C (do not alter)
- Pressure set point: Base + 15 Vacuum Units (typically 35)
- Pyrolysis Heater: 690 °C
- Setup ( ~0.5 hours)
1. Determine from log approximately how much Parylene C should be used to obtain desired thickness: Most current measurements suggest 30 grams for 10 microns across 12 wafers.
- Weigh out Parylene dimer using the scale in the cleanroom.
2. Fill out the log sheet. If you are doing Run 5, 10, 15, etc., check the “Parylene Machine Maintenance” document and notify superuser.
3. Check cold-trap, vaporizer door, and chamber lid o-rings to make sure each is clean and will form a good seal. If necessary, clean chamber lid o-ring by peeling off with tape and use only small amounts of Micro-clean and dry immediately afterwards to prevent damage to rubber. If you replace any o-rings, check for additional spares and order if necessary (see end of protocol for vendors). Also, notify superuser.
4. Do NOT remove the chamber base L-gasket unless you are having leak issues or you see Parylene pieces sticking out. Frequent removal and handling makes it crack sooner. Overtightening the c-clamp also makes it crack sooner.
5. Wipe all interior surfaces of the machine (chamber, lid, rotating table, bottom plate, baffle, etc.) and the cold trap probe with Micro-90, even if it was wiped down after the last run. Do not wipe the shelf, as this leaves TexWipe fibers that get coated over time and cause an irregular surface.
6. Place the flexicool cold trap probe into the coating systems cold trap.
7. Place the rotating shelf onto the base.
8. Cut 6 rectangular pieces of aluminum foil 8.5x4.5 inches, and place each piece in every shelf (alternating directions) to avoid holes in the back of the wafers.
9. Place your wafers onto the foil lined shelves. Two 100 mm diameter wafers can fit on each shelf.
10. Place a 1x3” clean, labeled glass slide on each shelf for thickness measurements.
11. Make sure none of the samples extend beyond the edge of the rotating table, as overhanging samples may hit the baffle when the table rotates.

12. Carefully lower the chamber around the shelf and place the chamber lid on top of the chamber.
13. Dimer boat construction:
Cut a rectangular piece of aluminum foil 11x4 inches, and form the aluminum piece lengthwise along the outside diameter of the boat form (metal tube). Face shiniest side of foil toward boat form. Fold in the ends of the foil, and remove the boat from the form. The dimer boat must be no more than 7.5 inches long
14. Pour Parylene C dimer pellets into the foil boat and load the boat into the vaporizer. Important: When loading the boat place it only as far into the vaporizer as necessary, do not push towards the back. Close and lock the vaporizer door.
- Running Parylene C System (minimum 2 hours)
15. Twist “Emergency Stop” button until it pops up.
16. Push the “Main Power” button. Wait for all the controllers on the display panel to come on and display current values.
17. Turn Vacuum knob to “Vacuum”. Initial Vacuum reading should be around 1000. Press down on the lid for the first 20 seconds to help make a good seal. It should reach ~100 in a couple of minutes. If not, your sample is off-gassing or there is a leak in the system.
18. Turn ON the chiller. Wait a minimum of 45 minutes before starting the deposition process.
19. Check that the vacuum level has reached at a level of 5 units (or lower). This may take up to 1 hour total if there are many items degassing. If the pump takes much longer there may be a leak.
Common leaks are caused by cracks or Parylene residue along the chamber O-ring or gasket, leaks along the O-ring within the chamber viewing window, leaks where the pressure sensor attaches to the tool (if replaced recently).
20. Turn on FURNACE and VAPORIZER, and press the PROCESS START/STOP button. The green button should now be illuminated. This will allow the furnace to begin heating up, however the process will not begin until pressure set points have been reached.
21. Wait for deposition.
In order for coating to begin, all the following must happen: 1) the chamber gauge must reach 135 °C, 2) the furnace must reach 690 °C, and 3) the vacuum reading must be less than 11. Then the vaporizer will begin heating, and the coating process will start. If any of the conditions are not met, something is wrong and you should contact the superuser.

22. The machine will run for several hours, depending on the coating thickness. The run will stop automatically and begin to cool down when the process is complete (green button will be blinking).
- Cool Down and Cleanup (~1 hour)
23. Let the system cool until the Vaporizer temperature is less than 90 °C to prevent harmful gasses from escaping.
24. Turn off the chiller and wait > 5 minutes.
25. Press the PROCESS START/STOP button.
26. Turn the left two switches to “Disable” and the vacuum switch to “Vent.”
27. Push the “Emergency Stop” button down.
28. Carefully remove cold-trap probe from machine and place in holder to defrost.
29. Remove the chamber lid.
30. Remove samples.
31. Peel Parylene C from the inside surfaces: chamber, lid, rotating table, bottom plate. if Parylene film is thin (< 3 microns, rainbow sheen) leave it until clean up after the next run.
32. Wipe inside surfaces with Micro-90 (except the shelf).
33. If necessary, clean chamber lid o-ring by peeling off with tape and use only small amounts of Micro-clean and dry immediately afterwards to prevent damage to rubber.
34. Open the vaporizer and discard the used foil boat.
35. PERFORM THIS STEP IN MAIN LAB: Once the probe is defrosted, use a green scotch brite pad to scrape off Parylene C residue from the cold-trap probe (outside and bottom), wipe clean with a TexWipe and Micro-90. If it doesn’t shine all over, you haven’t cleaned enough yet. Any cloudiness or residue will lead to rust spots, which is good for neither the probe nor the pump.
36. Put the probe back into the holder (NOT cold trap) for storage in between runs. If you incorrectly leave the probe in the cold trap, condensation build up can drip to the bottom and leave rust spots that are impossible to clean and bad for the machine.
37. Thickness Measurement

38. Use a new razor blade to cut a 1-2mm wide strip of Parylene off of one of the 1x3” glass slides from each shelf.
39. Measure deposition thickness with profilometer and update log.

### 4.2. High Resolution Lift Off Lithography

Tweezers: Use Teflon coated or plastic tweezers that are new or very clean, to avoid trapping dirt/impurities under first Parylene layer

1. Drybake wafer
- The aim of this step is to improve photoresist adhesion to Parylene by removing moisture.
- Bake the wafers in a vacuum oven at approximately 60 °C, under light vacuum (~½) atm and constant N2 flow.
- To achieve this, slowly open the vacuum valve while increasing nitrogen flow. Allow wafers to bake for > 15 minutes.
- Time: > 15 minutes
- Temperature: 60 C
- Pressure: 15" Hg
- Flow: 15 SCCM nitrogen
- Tool: Cascade Tek or Lindberg Blue vacuum oven
2. Mask Clean
- Safety: When handling Nanostrip or Piranha perform all steps in the ‘Acid Hood’. Wear full acid PPE: Apron, Mask, and Large Green Gloves. Keep hood sash below the height of any containers used.
- Fill the glass ‘Piranha Only’ beaker with a shallow layer of Nanostrip, just enough to cover a glass lithography mask (~⅛”). Place on top of a hotplate set to 60 °C. Set the old hot plate to 60 C. Prepare two HDPE trays with DI while you wait for the hotplate to heat.
- Using the ‘Piranha’ tweezers (no teflon, no plastic), carefully place your mask (feature side up) in the mask holder and then the mask holder into the glass beaker. Wait > 10 minutes -Carefully transfer the mask into the first tray and rinse briefly. Transfer to the second bath and rinse 5x with DI water. Rinse tweezers thoroughly as well.
- Blow mask dry with N2
- Turn off the hotplate and allow Nanostrip to cool to room temperature.

- Disposal: After cooling to room temperature carefully pour nanostrip into waste bottle using glass funnel. Triple rinse beaker. Triple rinse HDPE trays.
3. Photoresist spin (AZ 5214)
- Spin AZ 5214 photoresist to a thickness of ~1.2 microns
- Use at least three dummy spins
- Place the wafer in the spinner using the wafer centering tool. Deposit 2.5 mL of resist in the center of the wafer from a pre-prepared 3 mL syringe.
- Recipe: Program L
- 1st Spin Speed: 500 RPM
- 1st Spin Time: 5 seconds
- 2nd Spin Speed: 3200 RPM
- 2nd Spin Time: 40 seconds
- 2nd Spin Acceleration: 8 A.U (1088 RPM)
- Tool: Laurell Spinner WS-400/500B
4. Softbake
- Bake the wafer on a hotplate for 1 minute @ 110 °C Confirm temperature with IR gun. Typically requires setting the hot plate at 119 °C.
- Wafer should be placed in the center of the hot plate with the flat facing forward. Use a heat shield around the hot plate.
- After baking, store the wafer in black wafer storage box.
- Time: 60 seconds
- Temperature: 110 °C
- Tool: Lithography hood hotplate
5. First Exposure
- Set UV lamp; clean chuck and mask holder; place mask in holder using mask holder vacuum and clips.
- Set lamp to 12.5 mW/cm^2
- Set timer to 3.5 s → 42 mJ/cm^2 (measured i-line 365 nm)
- Expose under hard contact
- No o-ring
- Exposure Dose: 42 mJ/cm^22
- Time: 3.5 s
- Intensity: 12.5 mW/cm^2
- Mode: Hard Contact
- Tool: OAI Mask Aligner Series 200 Detailed steps for hard contact without alignment ❖ Load mask
❖ Turn ON mask vacuum and place set screws
❖ Clean mask with nitrogen
❖ Load wafer

❖ Turn ON substrate vacuum ❖ Clean wafer with nitrogen
❖ Turn ON nitrogen purge
❖ Lower mask
❖ Raise wafer till flush with mask ❖ Turn OFF substrate vacuum
❖ Turn ON hard contact
❖ Turn OFF nitrogen purge
❖ Wait ~30 seconds; you should see clear Newton rings at the interface of the wafer and mask.
❖ Expose
❖ Turn ON nitrogen purge and wait ~30 seconds
❖ Turn OFF hard contact
❖ Turn ON substrate vacuum
❖ Lower wafer chuck
❖ Raise mask
❖ Turn OFF substrate vacuum
6. Image reversal bake
- Bake the wafer on a hotplate for 63 seconds @ 110 °C Confirm temperature with IR gun. Typically requires setting the hot plate at 119 °C.
- Wafer should be placed in the center of the hot plate with the flat facing forward. Use a heat shield around the hot plate.
- Time: 63 seconds
- Temperature: 110 °C
- Tool: Lithography hood hotplate
7. Flood expose
- Exposure Dose: 280 mJ/cm^22
- Time: 23.3 s
- Intensity: 12.5 mW/cm^2
- Mode: Flood (no mask)
- Tool: OAI Mask Aligner Series 200
8. Develop
- After exposure, immediately place wafer in bath of DI water to avoid heating/reduce gas bubble formation for 2 minutes
- Prepare developer bath: 1:4 ratio of AZ340 to DI H2O in a shallow plastic tray marked for developer use 40 mL of developer and 160 mL of DI H2O for 200 mL total

- Place wafer in developer and apply mild agitation for 18 seconds
- Quench in wafer in DI bath and rinse gently 5x
- Blow wafer dry with nitrogen
9. Inspect
- Check feature marks, alignment marks under microscope with yellow light filter
- Check resist thickness, should be 1.1-1.3 microns

### 4.3. Metal Lift Off on Parylene C

PPE: Conduct lift-off only in fume hoods with sash lowered. Wafers should be lowered/raised from solvent baths using wafer dippers only. Cleanroom gloves and goggles required. Thick solvent gloves recommended.
Lift-off protocol for Pt stack
1. Prepare solvent baths
- All solvent baths should be prepared in glass beakers designated for lift-off, as the process generates metal microparticles that cannot be easily cleaned.
- Glass beaker on hotplate, set to 60 ºC, with small layer of NMP/PG remover
- Glass beaker at room temperature with small layer of NMP/PG remover
- Glass beaker at room temperature with large amount of isopropanol
- Glass beaker or HDPE tray with DI water
2. Warm NMP soak
- 20-40 minute soak in warm (60 ºC) NMP. Features should begin to appear after a few minutes. If not, the photoresist profile may be incorrect.
- After 20 minutes spray with NMP from a squeeze bottle. Devices should be completely resolved before moving to next bath.
3. NMP rinse
- Transfer wafer to the room temperature NMP bath.
- While holding the wafer at a downward sloping angle, spray vigorously with an NMP squeeze bottle to remove all remaining metal flakes.
- Rinse any remaining metal flakes in the NMP bath for ~5 minutes.
4. IPA Rinse
- Transfer wafer to the room temperature IPA bath.
- While holding the wafer at a downward sloping angle, spray vigorously with an IPA squeeze bottle to remove all remaining metal flakes.
- Soak in IPA bath for 10 minutes
5. DI Rinse
- Soak wafer in DI water bath. Rinse ~3-5x with DI water.
6. Dry
- Blow dry wafer with nitrogen.
- Dry-bake wafers for > 15 minutes
- Time: > 15 minutes
- Temperature: 60 C

- Pressure: 15" Hg
- Flow: 15 SCCM nitrogen
- Tool: Cascade Tek or Lindberg Blue vacuum oven

### 4.4. A-174 Adhesion Promoter Treatment

- Overview
Native Parylene has low adhesion to metal surfaces. Pretreating the metal surface with A-174 silane (Gamma-Methacryloxypropyltrimethoxysilane, CAS# 2530-85-0, Special Coating System, Indianapolis, IN, USA) prior to Parylene deposition can significantly increase the Parylene-metal bonding. A-174 is a liquid that needs to be mixed with IPA and DI water in a specific ratio and then sit for at least 2.5 hours to fully react before usage.
1. Prepare solution
- Do all work in a fume hood. Prepare a mixture of 900 mL DI water, 900 mL isopropanol, and 9 mL A-174 Silane in a large glass beaker. Mix carefully with a glass stirring rod. Cover top with aluminum foil.
- Allow the mixture to sit for at least 2.5 hours, but no more than 24 hours.
2. Soak wafers
- Decant the mixture into the large crystallizing dish labeled for A-174 use. Place your wafers face side up into the corresponding wafer cassette. Lower the cassette into the solution and ensure all the wafers are fully submerged.
- Soak for 30 minutes.
3. Rinse samples
- Remove the wafers and place on Tex-Wipes in the fume hood face up. Allow to air dry for 30 minutes. Then rinse the wafers thoroughly with an isopropanol squeeze bottle for 30 minutes. Blow dry with nitrogen.
4. Clean up
- Dispose of remaining solution in solvent waste. Rinse all equipment with isopropanol and DI water.
5. Coat samples
- Wafers should be coated with Parylene within 12 hours after A-174 treatment.

### 4.5. RIE Etch Mask Lithography

1. Clean Parylene coated wafers
- Solvent clean wafers in sequential baths of room temperature acetone, isopropanol, and DI water. Blow dry. Solvent clean may be skipped if the wafer was cleaned recently as the final step from a previous process.
- Expose wafers to oxygen plasma
- Time: 300 seconds
- Temperature: Room temperature
- Pressure: 125 mTorr
- Power: 100 W
- Flow: 30 SCCM O2
- Tool: YES Asher
2. Dry-bake Parylene wafers
- The aim of this step is to improve photoresist adhesion to Parylene by removing moisture.
- Bake the wafers in a vacuum oven at approximately 60 °C, under light vacuum (~½) atm and constant N2 flow. Allow wafers to bake for > 15 minutes.
- Time: > 15 minutes
- Temperature: 60 C
- Pressure: 15" Hg
- Flow: 15 SCCM nitrogen
- Tool: Cascade Tek or Lindberg Blue vacuum oven
3. Photoresist spin (AZ 12XT-20PL-15)
- Spin AZ 12XT-20PL-15 photoresist to a thickness of 14-15 microns
- Use at least three dummy spins
- Place the wafer in the spinner using the wafer centering tool. Deposit 2.5 mL of resist in the center of the wafer from a pre-prepared 3 mL syringe.
- Recipe: Program T
- 1st Spin Speed: 500 RPM
- 1st Spin Time: 10 seconds
- 1st Spin Acceleration: 5 A.U.
- 2nd Spin Speed: 2000 RPM
- 2nd Spin Time: 45 seconds
- 2nd Spin Acceleration: 8 A.U (1088 RPM)
- Tool: Laurell Spinner WS-400/500B
4. Remove the Edge bead using the protocol on section 4.6.
5. Softbake

- Bake the wafer on a hotplate for 3 minutes @ 110 °C Confirm temperature with IR gun. Typically requires setting the hot plate at 119 °C.
- Wafer should be placed in the center of the hot plate with the flat facing forward. Use a heat shield around the hot plate.
- Time: 3 minutes
- Temperature: 110 °C
- Tool: Lithography hood hotplate
6. Align and expose
- Set UV lamp; clean chuck and mask holder; place mask in holder using mask holder vacuum and clips.
- Set lamp to 10 mW/cm^2
- Set timer to 18.5 s → 185 mJ/cm^2 (measured i-line 365 nm)
- Expose under soft contact
- No o-ring
- Exposure Dose: 185 mJ/cm^22
- Time: 18.5 s
- Intensity: 10 mW/cm^2
- Mode: Soft Contact
- Tool: OAI Mask Aligner Series 200
- Alternative exposure using Heidelberg Direct Write Laser 66+ tool
- Laser Power: 230 mW
- Intensity: 100%
- Filter: 100%
- Exposure Count: 2
- Focus Offset: 0%
- Tool: Heidelberg DWL 66+ Detailed steps for soft contact with alignment ❖ Load mask
❖ Turn ON mask vacuum and place set screws ❖ Clean mask with nitrogen
❖ Load wafer
❖ Turn ON substrate vacuum
❖ Clean wafer with nitrogen
❖ Turn ON nitrogen purge
❖ Lower mask
❖ Raise wafer till flush with mask (check with microscope, 2nd objective lens)
❖ Turn ON ball lock
❖ Lower sensitivity of the z-axis adjust to < 20 mA, then lower wafer slightly so it no longer contacts mask
❖ Moving back and forth between left and right alignment marks, align the angle (theta) of the mask and wafer.
❖ Once wafer and mask are aligned in theta, ensure X and Y coordinates are aligned.

❖ Once satisfied, raise the wafer to contact, confirm alignment has not drifted. ❖ Expose
❖ Lower wafer until no longer in contact
❖ Raise sensitivity back to 25 mA, lower wafer fully
❖ Raise mask
❖ Turn OFF substrate vacuum; Turn OFF ball lock
7. Post Exposure Bake
- Bake the wafer on a hotplate for 1 minute @ 90 °C Confirm temperature with an IR gun. Typically requires setting a hot plate at 98°C.
- Wafer should be placed in the center of the hot plate with the flat facing forward. Use a heat shield around the hot plate.
- Time: 1 minute
- Temperature: 90°C
- Tool: Lithography hood hotplate
8. Develop
- Develop in bath of 726 MIF (undiluted) for 75 seconds with mild agitation
- For DWL 66+ exposure allow up to 120 seconds with mild agitation
- A single bath should be able to process 6 wafers
- Important: Time may fluctuate with mask design, you will need to watch for your features to develop by eye and calibrate for different processes.
- Rinse in DI >3x times
- Dispose of used developer in designated waste bottle in acid/base hood
9. Inspect
- Check feature marks, alignment marks under microscope with yellow light filter
- Check resist thickness, should be 14-15 microns

### 4.6. Edge Bead Removal

1. Prepare spinner
- Place and center wafer on Laurell spinner. Typically this protocol is performed immediately following photoresist spinning and so this step is unnecessary.
- Carefully lower EBR shield (black plastic cylinder) over the wafer, without touching the wafer. With the spinner lid still open, place the magnet over the lid sensor to override the interlock. If necessary use double sided tape to hold magnets in place.
2. Prepare EBR solvent
- Fill a small glass beaker with EBR solvent and soak a large microfiber swab with solvent.
3. Program spinner

- Recipe: Program E
- 1st Spin Speed: 200 RPM
- 1st Spin Time: 5 seconds
- 2nd Spin Speed: 750 RPM
- 2nd Spin Time: 40 seconds
- Tool: Laurell Spinner WS-400/500B
4. Edge Bead Removal
- Turn the wafer such that the flat faces ‘3 o’clock’. Blot away excess solvent from the swab and place it on the edge of the wafer such that the swab is only just in contact with the edge bead. Start the program and use the first 5 seconds to reposition the swab if necessary. After 20 seconds, retract the swab and allow the wafer to spin dry.
5. Repeat if necessary

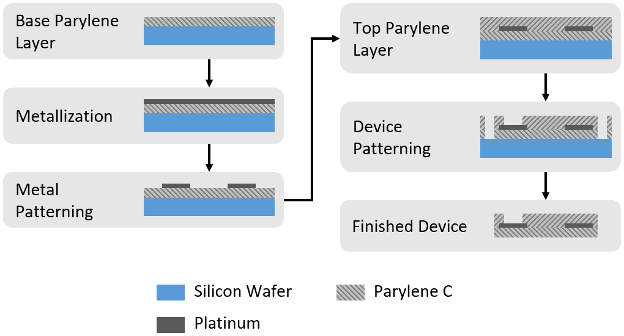
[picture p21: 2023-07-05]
Parylene Cuff Electrode/Fabrication and Packaging/Process flow diagram.png

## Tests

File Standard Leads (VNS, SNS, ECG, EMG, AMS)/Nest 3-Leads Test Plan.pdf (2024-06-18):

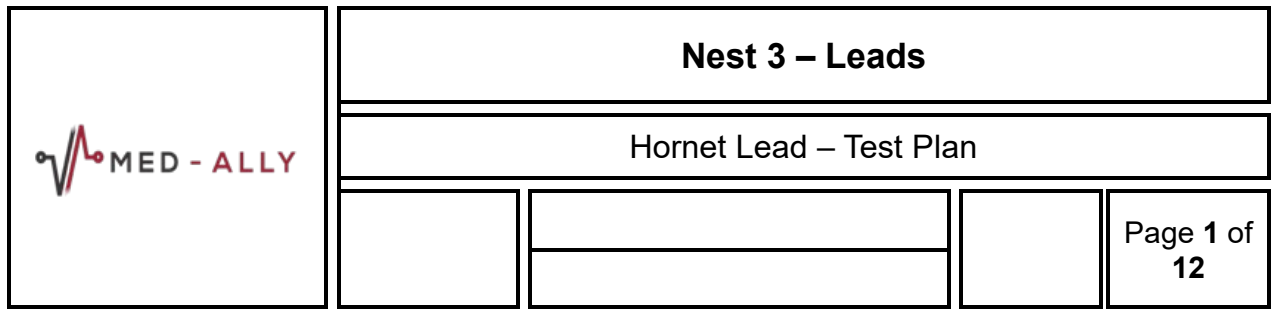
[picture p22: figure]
Nest 3 – Leads; Hornet Lead – Test Plan; Page 1 of 12

### 1. Purpose

The purpose of this document is to summarize how The Hornet Leads will be tested to show that the design, construction and functionality of the device meets design and functionality requirements and complies with applicable standards.

### 2. Scope

This document is valid for the Hornet Leads. The test plan outlined in this document is progressive and may be released at various stages prior to finalization. This document includes an overview of applicable testing requirements, equipment, and documentation.

### 3. References

Document No. | Title
ISO 14708-1 & 3 | Implants for surgery – Active Implantable Medical Devices
| ISO 11607-1:2006 and ASTM F1980-07(2011)
BS EN 45502-2-1:2003 | Active Implantable Medical Devices Part 2-1: Particular requirements for active im-plantable medical devices intended to treat bradyarrhythmia (cardiac pacemakers)

### 4. Definitions

Abbreviation or Term | Definition
DVT | Design Verification Test
Engineering Bench Level Test | Also known as Engineering Design Verification. Prototype samples are created and subjected to internal and external testing to verify that design requirements and specifications are being met. The results from these tests will determine if the product gets released to Production.
IPG | Implantable Pulse Generator

### 5. General Description of Product

The CARRS system is an open source system to enable developments in stimulation and sensing technologies. The system is capable of closed loop stimulation and sensing or can be used independently. The system components are: external charger and controller, implantable pulse generator, collection of interoperable and implantable leads. This document is focused on leads only.

### Hornet Lead – Test Plan

### Page 2 of 12

CONFIDENTIAL
All information contained in this document is confidential and is the sole property of Med-Ally Inc. Any reproduction in part or whole without the written permission of Med-Ally Inc. is prohibited

### 6. Methods

Each test will be summarized via an approved quality management system controlled protocol. The test will be conducted per the protocol with records and deviations recorded. Results and conclusions along with any needed discussion and recommendations will be documented in a report. The test results will be compiled and summarized in a Test Report or appendix.

### 7. Sample Size Strategy

Three to nine samples for each test will be used. This number is to show the ability of the lead to meet the shown criteria. For formal DVT testing for human use these values will need to be reviewed per use case based on risk and application to evaluate if test and sample size can be utilized or if the test needs to be supplemented or repeated. Planned testing units are represented below for each test.

### 8. DVT Test Details 8.1. Tests that require pre-conditioning

8.1.1. Baseline functional lead measurements shall be recorded and cataloged.
8.1.2. Ensure measurements for each lead it clearly identifiable.
8.1.3. Preconditioning protocol:
8.1.3.1 Pre-conditioning bath of 9 g/l saline at 37 deg C +/- 5 deg C submerged for 10 days. 8.1.3.2 Immediately prior to testing the lead shall be rinsed in distilled or deionized water, and then wiped free of surface water.
Test | Testing Details
Lead Body Pull Test at 5 N | Purpose | ►Leads shall withstand the tensile forces that might occur after implantation, without fracture of any conductors or joints or breaching of any functional electrical isolation.
| Standards | ►ISO 14708-2:23.3
| Acceptance Criteria | ► Leads exhibits no permanent elongation in exceeds of 5% nor any permanent functional damage; ►The continuity measurements do not change from baseline to after conditioning; ►The leakage current measured between each conductor and the reference electrode and between any two conductors that have an exposed conductive surface intended for contact with tissue is <= 2 mA during the voltage application.
| Equipment | ►preconditioning bath of approximately 9 g/l saline at 37 deg C +/- 5 °C, ►a tensile load tester,

### Hornet Lead – Test Plan

### Page 3 of 12

CONFIDENTIAL
All information contained in this document is confidential and is the sole property of Med-Ally Inc. Any reproduction in part or whole without the
Test | Testing Details
| | ►a resistance meter, ►a reference electrode plate having a noble metal surface with a minimum area of 500 mm2 that can be located in the test bath (same as precondition-ing bath requirements) ►a leakage current tester, capable of applying 100 V and supplying a current of at least 2 mA.
| Lead Samples | ►20 cm SNS leads will be utilized. ►SNS lead was chosen because the quadripolar leads represent the worst case of lead body stresses with 4 filar vs. 2 filar. ►Qty 9 as representative samples will be used.

Test Set Up

►After conditioning:
►The LEAD shall be fitted in the tensile tester, clamped at the metallic surface of the LEAD connector pin and at the appropriate point on the distal end of the LEAD. The distance between the lamping points shall be measured.
- The lead shall be subjected to a tensile load, limited to a value causing 20% elongation, otherwise increased to at least 5N. The tensile load shall be sustained for at least 1 min, then relieved.
►The tensile load application shall be repeated for each combination of distal end tip and lead connector pin. This may be accomplished by using multiple leads as the test sample.
►The electrical continuity of each conduction path shall be verified by measuring DC resistance
►The insulation integrity of each lead shall be verified by immersing the outer covering, other than 20 mm of any exposed conductive surface, in the test bath. The test specimen(s) shall be placed in the test bath within 30 min of removal from the preconditioning bath and shall be immersed in the test bath for a minimum of 1 h before proceeding. The test specimen shall be positioned in the test bath so that the lead body is not less than 50 mm nor more than 200 mm from the reference electrode plate.
►The insulation shall then be subjected to a 100 V +/- V DC test potential between each conductor and the reference electrode and between any two conductors that have an exposed conductive surface intended for contact with tissue. The test voltage shall attain the full value within 0,1 s to 5 s. The test potential shall be maintained at full value for at least 15 s before being lowered to zero.
Report ► Generate Report

### Hornet Lead – Test Plan

### Page 4 of 12

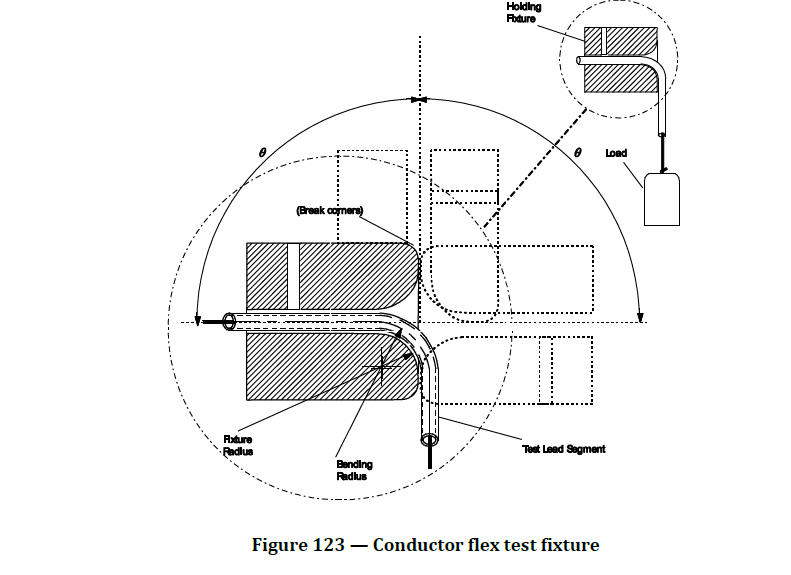
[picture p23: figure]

CONFIDENTIAL
All information contained in this document is confidential and is the sole property of Med-Ally Inc. Any reproduction in part or whole without the
Test | Testing Details
| Purpose | ►Implantable leads shall withstand the flexural stresses that might occur after implantation, without fracture of any conductor. ►Test 1 to be conducted to be conducted 5 cm from the connecting features of stimulation or sensing on the distal end on lead body. ►Test 2 to be conducted on each type of uniform lead body on the proximal end construction for each lead type.
| Standards | ►ISO14708-2:23.5
| Acceptance Criteria | ► Measured resistance and conductance has not significantly varied from baseline values.

Lead Flexure
Cycling Test

Equipment

►a resistance meter,
►functional test equipment ►Figure 123 Test fixture:

►Figure 124 Test Fixtures

### Hornet Lead – Test Plan

### Page 5 of 12

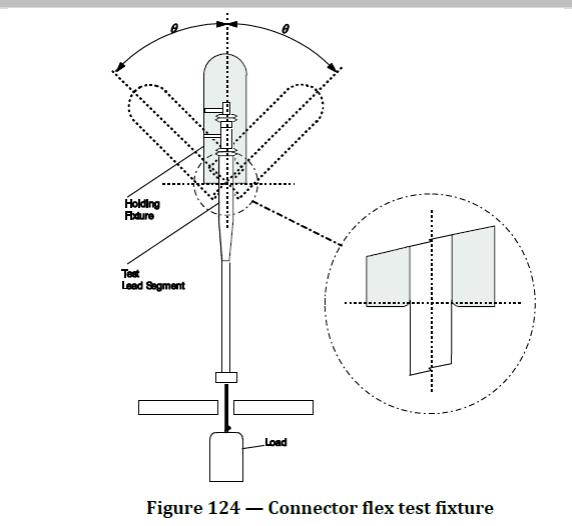
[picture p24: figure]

CONFIDENTIAL
All information contained in this document is confidential and is the sole property of Med-Ally Inc. Any reproduction in part or whole without the
Test | Testing Details

Lead Samples

►20 cm leads will be utilized.
►Qty 3 SNS leads as representative samples will be used of a quadripolar lead body and Qty 3 Cuff/VNS lead samples will be used of a bipolar lead body sample.
►A mix of SNS (4 filar) and VNS leads (2 filar) will be utilized to compare representative samples for both lead configurations. The test plan can be used across different lead applications due to the test purpose as outlined above.

Test Set Up

►Perform preconditioning
Test 1: Flexible lead segments – 5 cm from distal end
►Using special holding fixture (see figure 123 from standard). The inside bore of the fixture shall be no greater than 110% of the diameter of the lead segment under test. At the lower end of the fixture, the inside surface shall be formed into a bell mouth having a radius such that, when the test segment conforms to the contour of the fixture, the center line of the test segment forms a 6 mm +/- 0.1 mm center line bending radius
►The fixture shall be mounted in a machine that can oscillate the fixture 90 +0/-5 degrees from the vertical and forces the test segment to flex in the bell mouth of the fixture. The lead test segment shall be mounted to hang vertically under gravity in the holding fixture, oriented in the worst-case test condition when the test segment allows multiple orientations. A load sufficient to ensure that the center line of the test segment conforms to the bending radius shall be attached to the lower end of a thin, flexible line (cord) strung through the test segment. For LEAD bodies with no accessible

### Hornet Lead – Test Plan

### Page 6 of 12

CONFIDENTIAL
All information contained in this document is confidential and is the sole property of Med-Ally Inc. Any reproduction in part or whole without the
Test | Testing Details lumen, a minimal tensile load may be applied directly to the test segment, so that it conforms to the bending radius. ►The fixture shall be oscillated through an angle 90 degrees +0/-5 deg each side of vertical at a rate of approximately 2 Hz for a minimum of 47,000 cycles. (minimize vibration). ►The test shall be repeated for each unique uniform flexible part of the lead body. ►Post flexure measure resistance and functional conductivity Test 2: Lead proximal connector joints between lead and connector body – proximal end ► Using special holding fixture (see figure 124 from standard) (similar in form to header). The holding fixture shall be made of rigid materials with representative corners and materials to header. ►The holding fixture shall be mounted in a machine that can rotate the fixture 45 deg +/- 2 deg from the vertical (figure 124 from standard). The center of rotation shall be in the plane where the rounded corners of the holding fixture begin. The holding fixture shall allow the lead connector an attached lead segment to hang vertically under gravity. The lead connector shall be fitted into the holding fixture, oriented in the worst-case test condition and retained by the set screw mechanism. ►A load shall be attached to the lead segment 10 cm +/- 0.5 cm from the center of rotation of the holding fixture. The load attachment mechanism shall ensure that there is no relative motion between the conductor and the tubing at the point of attachment. The load shall be 100 g +/- 5 g (including the attachment mechanism). ►The holding fixture shall then be oscillated 45 deg +/- 2 degrees each side of vertical at a rate of approximately 2 Hz for a minimum of 82,000 cycles. ►The test shall be repeated for each joint in the lead body. ►Post flexure measure resistance and functional conductivity
Report | ►Generate Report
Qualification Test | Testing Details
Lead Connector | Purpose | ► Demonstrate the retention force provided by the implantable connector shall be greater than or equal to 10 N. For the lead to header and lead to

### Hornet Lead – Test Plan

### Page 7 of 12

CONFIDENTIAL
All information contained in this document is confidential and is the sole property of Med-Ally Inc. Any reproduction in part or whole without the
Qualification Test | Testing Details
Pull Test at 10 N | interconnect.
Standards | ►ISO 14708-2: 23.6
Acceptance Criteria | ►The lead shall not be disconnected at value of 10 N or less.
Equipment | ► The insertion and removal force will be measured by the Instron S/N 3367Q1264. ► Saline bath, approximately 9 g/l at 37oC ± 5oC
Lead Samples | ►20 cm leads will be utilized. ►Qty 3 SNS leads as representative samples will be used of a quadripolar lead body and Qty 3 Cuff/VNS lead samples will be used of a bipolar lead body sample. ►A mix of SNS (4 filar) and VNS leads (2 filar) will be utilized to compare representative samples for both lead configurations. The test plan can be used across different lead applications due to the test purpose as outlined above.
Test Set Up | ► The implantable connector pair shall be mated and immersed in a saline bath, approximately 9 g/l at 37oC ± 5oC, for a minimum of 10 days. ► Remove the lead from the saline bath. ► Subject the lead to header to straight pull of 10 N +/- 0.5 N for a minimum of 10 seconds.
Report | ►Generate report

### 8.2. Tests that DO NOT require pre-conditioning

8.2.1. Baseline functional lead measurements shall be recorded and cataloged.
8.2.2. Ensure measurements for each lead it clearly identifiable.
Qualification Test | Testing Details
Lead leakage current < 10 uA | Purpose | ► To test that the lead has effective functional electrical insulation between conductors.
| Standards | ►ISO 14708-2: 16.1 / IEC 60601-1, IEC 62353
| Acceptance Criteria | ►The leads must have no more than 100 uA current leakage when tested to a minimum of 50 V DC in normal condition (NC). ► Type BF – Electrically connected to Patient but not directly to heart

### Hornet Lead – Test Plan

### Page 8 of 12

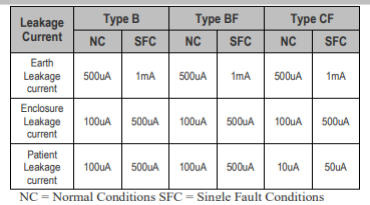
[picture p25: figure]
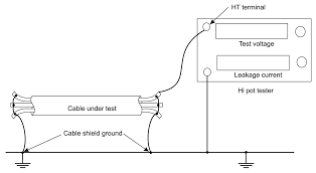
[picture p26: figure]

CONFIDENTIAL
All information contained in this document is confidential and is the sole property of Med-Ally Inc. Any reproduction in part or whole without the
Qualification Test | Testing Details
Equipment | ► Guardian Electrical Safety Analyzer model 19032 from Chroma System Solutions to measure current leakage.
Lead Samples | ►20 cm leads will be utilized. ►Qty 9 SNS leads as representative samples will be used of a quadripolar lead body as the worst case sample.
Test Set Up | ► High and low leakage current limits will be set to 1 mA. The applied voltage will be set to 50 V DC.
Report | ►Generate Report
Qualification Test | Testing Details
Lead DC Charge <= 0.75 UA/mm² | Purpose | ►To confirm the maximum current density at any electrode is no more than 0.75 uA/mm² . Except for its intended function, an IMPLANTABLE PULSE GENERATOR, when in use, shall be electrically neutral. No d.c. leakage current of more than 1 μA shall occur in any of the current pathways of the CASE TERMINALS and no more than 0.1 μA in the current pathways of any other TERMINAL.
| Standards | ►ISO 14708-2: 16.2

### Hornet Lead – Test Plan

### Page 9 of 12

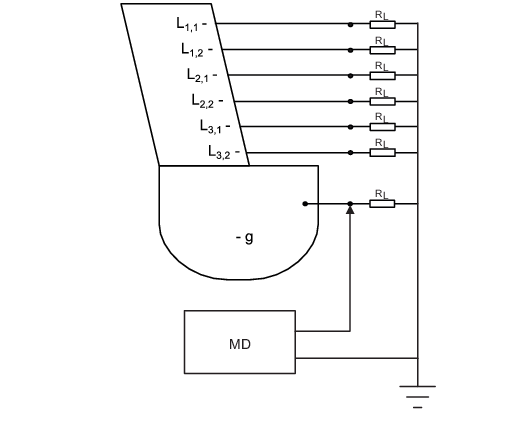
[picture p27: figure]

CONFIDENTIAL
All information contained in this document is confidential and is the sole property of Med-Ally Inc. Any reproduction in part or whole without the
Qualification Test | Testing Details
| Acceptance Criteria | ► maximum current density at any electrode is no more than 0.75 uA/mm² except for its intended function.
| Equipment | ► Guardian Electrical Safety Analyzer model 19032 from Chroma System Solutions to measure current leakage.
| Lead Samples | ►40 cm leads will be utilized. ►Qty 9 VNS leads as representative samples will be used of a cuff lead sam-ple as this is the most likely to use high frequency signals, which represents the highest risk for lead DC charge.

Test Set Up

- The IMPLANTABLE PULSE GENERATOR shall be set to the nominal settings recommended by the MANUFACTURER (i.e. the “factory recommended settings”) but with the PULSE AMPLITUDE and PULSE DURATION programmed to the highest available settings.
►Each electrically conductive part of the IMPLANTABLE PULSE GENERATOR in contact with body tissue when the device is implanted shall be identified and connected to a common bus through 500 1 % load resistors RL (see Figure 122). For devices with fewer terminals than shown in Figure 122, the associated resistors RL are not used.

Example image:

►Measure the average direct voltage across each load resistor with the measuring device. Steady-state conditions shall be reached before the measurement is made.
►The measurement of the individual terminal currents may be made with a plurality of measuring devices.

### Hornet Lead – Test Plan

### Page 10 of 12

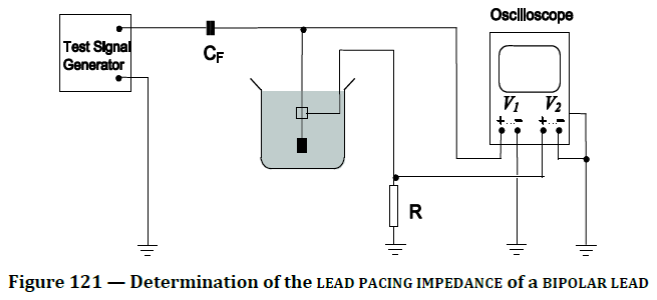
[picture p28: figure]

CONFIDENTIAL
All information contained in this document is confidential and is the sole property of Med-Ally Inc. Any reproduction in part or whole without the
Qualification Test | Testing Details
| Report | ►Generate report
Qualification Test | Testing Details
| Purpose | ►Measurement of lead stimulating impedance using in vitro approach
| Standards | ► ISO 14708-2: 6.2.3
| Acceptance Criteria | ►Resistance is acceptable. Typically < 50 ohms.
| Equipment | ►Oscilloscope ►Test Signal Generator
| Lead Samples | ►40 cm leads will be utilized. ►Qty 9 VNS leads as representative samples will be used of a cuff lead sample with the DC charge test.

Lead contact
impedance < 1000
ohm

Test Set Up

- The LEAD shall be inserted into the test body so that the ELECTRODES are at least 10 mm from any fluid boundary.
►The test signal generator shall be connected through a 33 μF +/- 5 % series film capacitor (CF) to the LEAD, the metal plates and the oscilloscope as shown in Figure 121.

►Set the signal generator to provide negative pulses, 65 +/- 5 per minute, amplitude 4 V+/-0.1 V and duration (Tp ) of 0.5 ms +/- 0.05 ms. The LEAD current shall be determined by measuring the voltage drop across the 10

### Hornet Lead – Test Plan

### Page 11 of 12

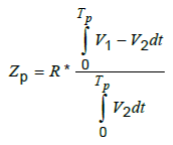
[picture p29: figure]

CONFIDENTIAL
All information contained in this document is confidential and is the sole property of Med-Ally Inc. Any reproduction in part or whole without the
Qualification Test | Testing Details
| | ohm +/- 2 % resistor. ►The LEAD stimulation IMPEDANCE (Zp) shall be calculated, using the mean values of voltage and current, by applying the formula: NOTE See Figure 120 and Figure 121 for definitions of V1 and V2.
| Report | ► Generate Report
Qualification Test | Testing Details
| Purpose | ►Ensure Leads meet requirements, standards, and performance characteristics for the 2 years.
| Standards | ►ISO 14708-1:19-1
| Acceptance Criteria | ►Meets functional specifications at appropriate time points. ►There is no visible corrosion or delamination apparent that would lead to connection of two conducting surfaces. ►No unacceptable risks become evident as the device ages.
| Equipment | ►Oven ►RH Meter ►Timer ►Temperature Probe and Meter
| Lead Samples | ►20 cm leads will be utilized. ►Qty 9 VNS leads as representative samples will be used of a cuff lead sample with the DC charge test.
| Test Set Up | ►Consider the composition, morphology, thermal transitions, additives or other chemical properties present in materials. ► Assumptions: - Conditioned in 0.9% sodium chlorine bath heated to 55 degrees C per accelerated aging standards outlined in ISO 11607-1:2006 and ASTM F1980-07(2011)

Lead accelerated
aging test

### Hornet Lead – Test Plan

### Page 12 of 12

CONFIDENTIAL
All information contained in this document is confidential and is the sole property of Med-Ally Inc. Any reproduction in part or whole without the
Qualification Test | Testing Details
- Accelerating Aging Temperature 55 degrees C
- Nominal temperature 37 degrees C
- Q10 value of 2.0
- With the above calculations the testing timepoints:
| • 3 months = 26 days • 12 months = 52 days • 24 months = 105 days • 36 months = 314 days • 48 months = 419 days • 60 months = 524 days
- Team may decide to increase temperature depending on timepoint
| calculation will change accordingly ►Place the Aging Parts in prepared saline bath and place in designated oven and record start time and date. Record temperature measurement calibration information. ►Age Samples at Accelerated Aging Temperature, and in parallel, age samples at room temperature. ►At the end of each Aging Test Time Interval, visually inspect device and verify performance requirements of the device. Place device back in chamber after testing to continue the conditioning.

Report

| ►Generate Report, including aging conditions (test temperature, humidity, cycle, ambient temperature, time frame, sample sizes, time intervals of sampling, and specific tests at each time interval). Record all instruments used and calibration information. Document test standard references and

methods of evaluation.

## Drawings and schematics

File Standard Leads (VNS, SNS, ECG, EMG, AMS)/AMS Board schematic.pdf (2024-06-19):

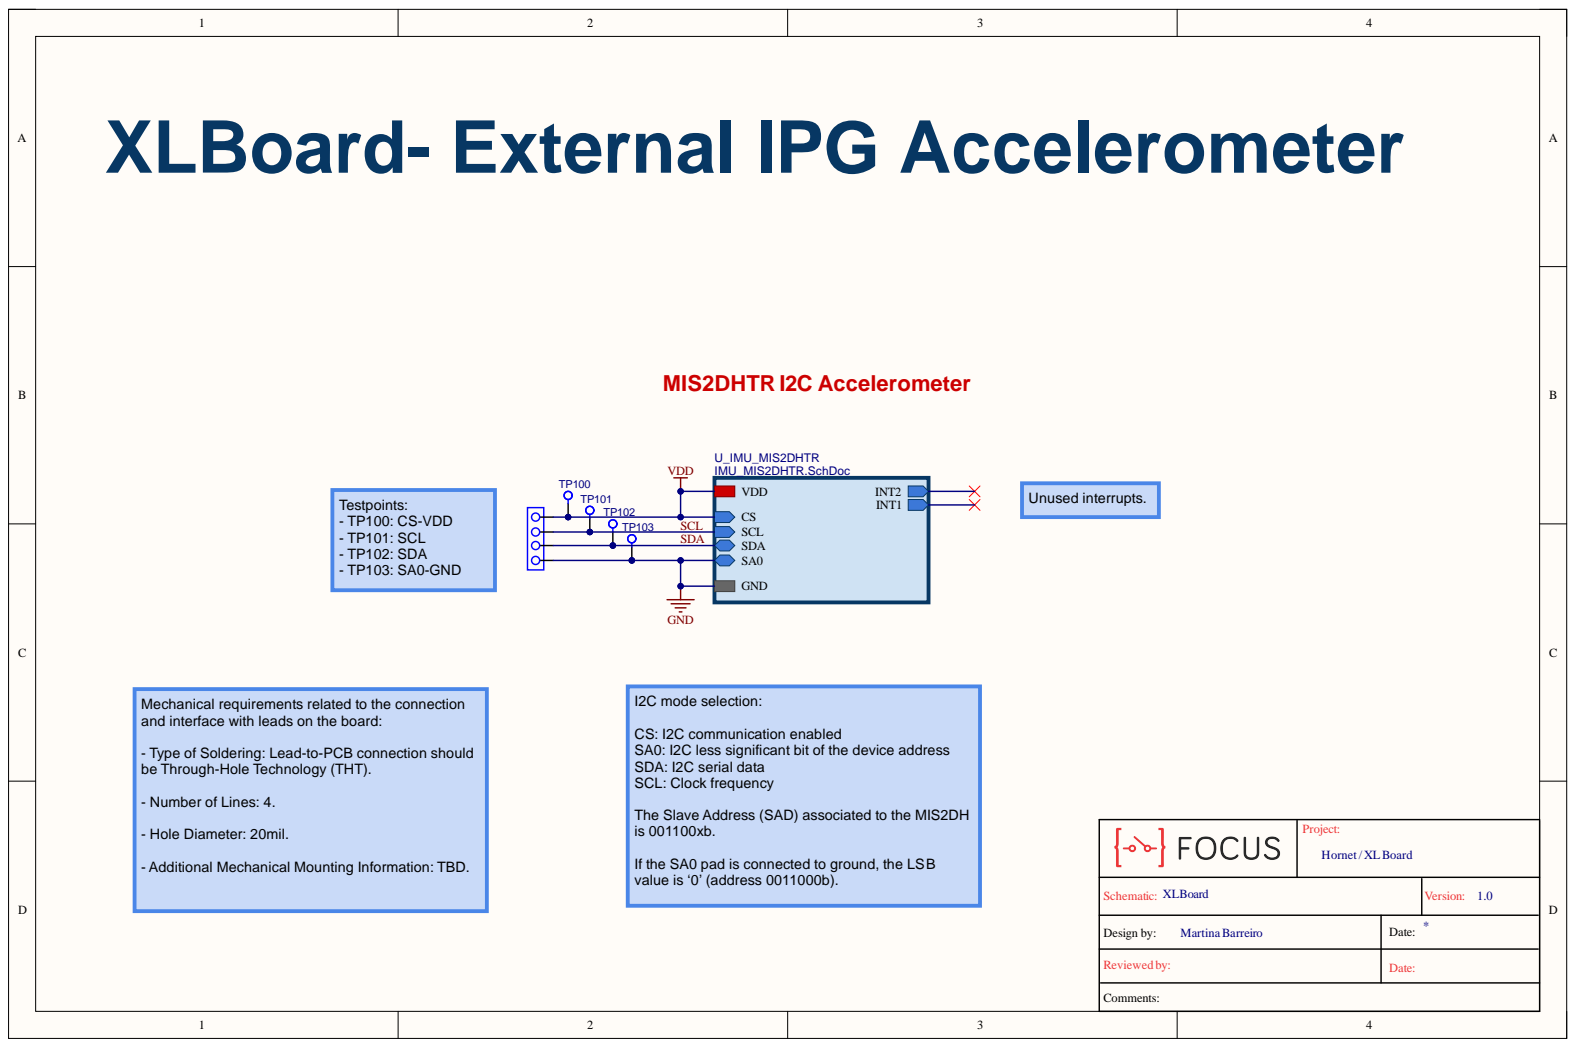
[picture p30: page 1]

XLBoard- External IPG Accelerometer

SCL TP103

SDA

Mechanical requirements related to the connection
and interface with leads on the board:

I2C mode selection: CS: I2C communication enabled

- Type of Soldering: Lead-to-PCB connection should
be Through-Hole Technology (THT).

SA0: I2C less significant bit of the device address
SDA: I2C serial data
SCL: Clock frequency

The Slave Address (SAD) associated to the MIS2DH is 001100xb.

Project: Hornet / XL Board

- Additional Mechanical Mounting Information: TBD.

If the SA0 pad is connected to ground, the LSB
value is

Schematic: XLBoard | Version: 1.0

Design by: Martina Barreiro | * Date:

Date:

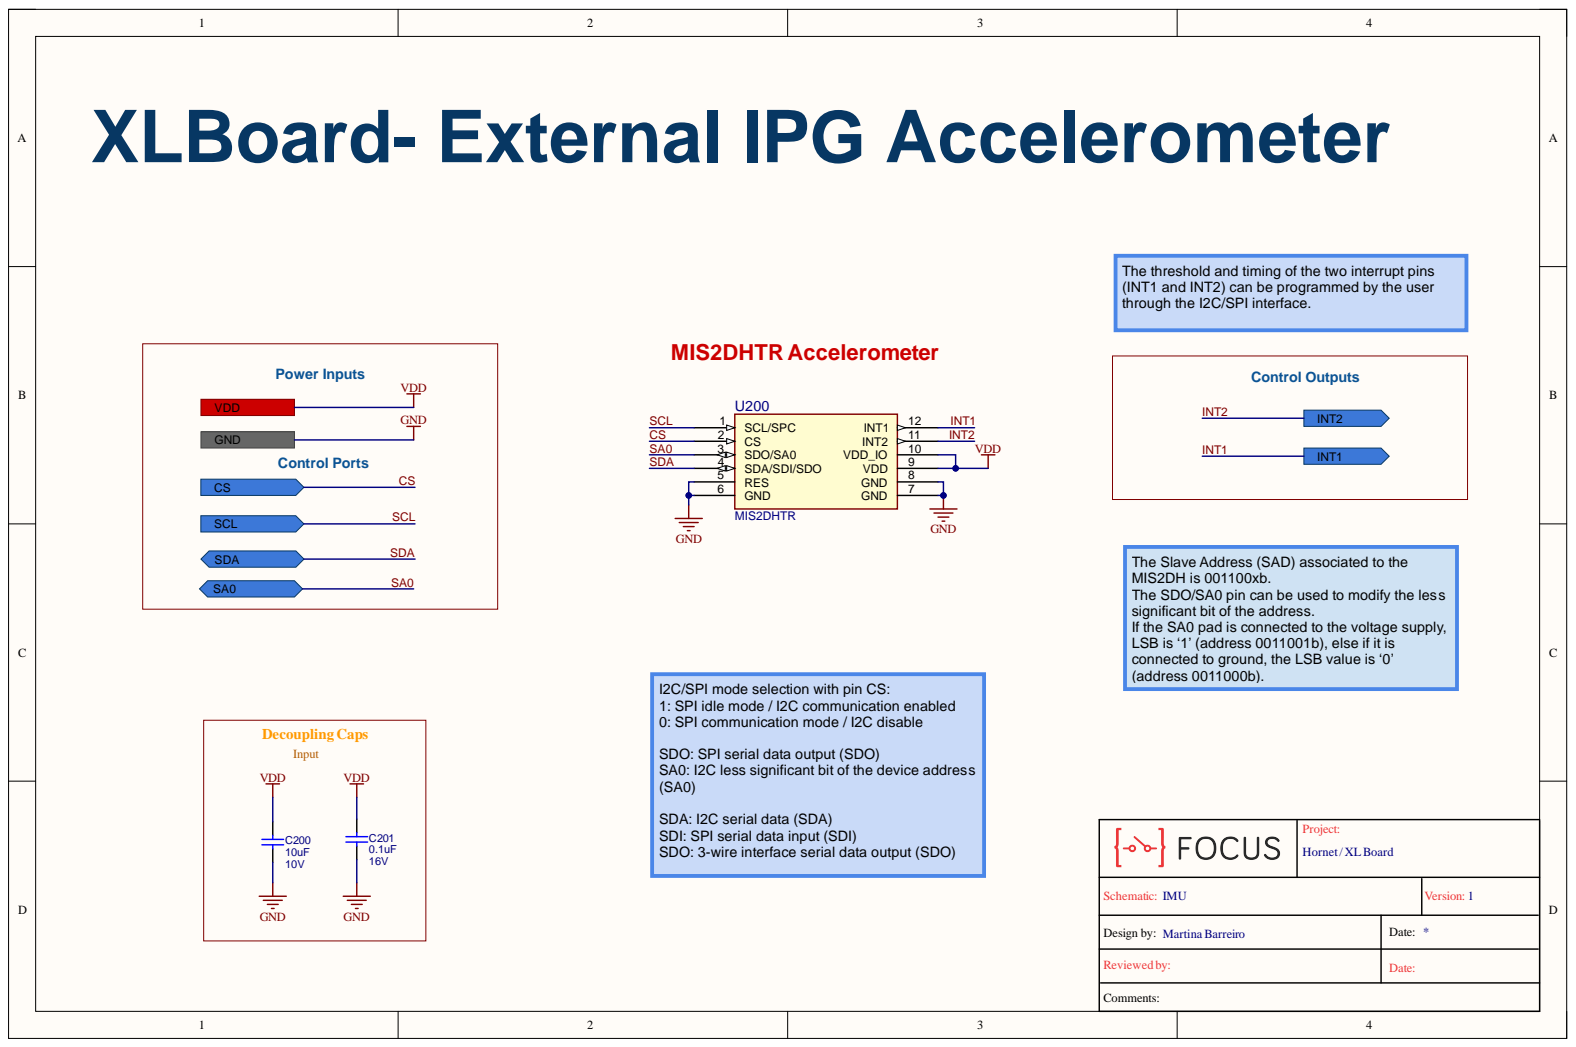
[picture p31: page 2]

P roje c t : Boa r d

S chema ti c : IMU | Ve rsio n : 1

Design by: Reviewed by Ma rtina B a r r e ir o | Da te : *

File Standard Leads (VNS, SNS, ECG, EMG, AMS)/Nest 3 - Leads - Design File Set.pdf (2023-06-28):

# DRAFT

ITEM NO. | PART NUMBER | DESCRIPTION | QTY. | | REVISIONS

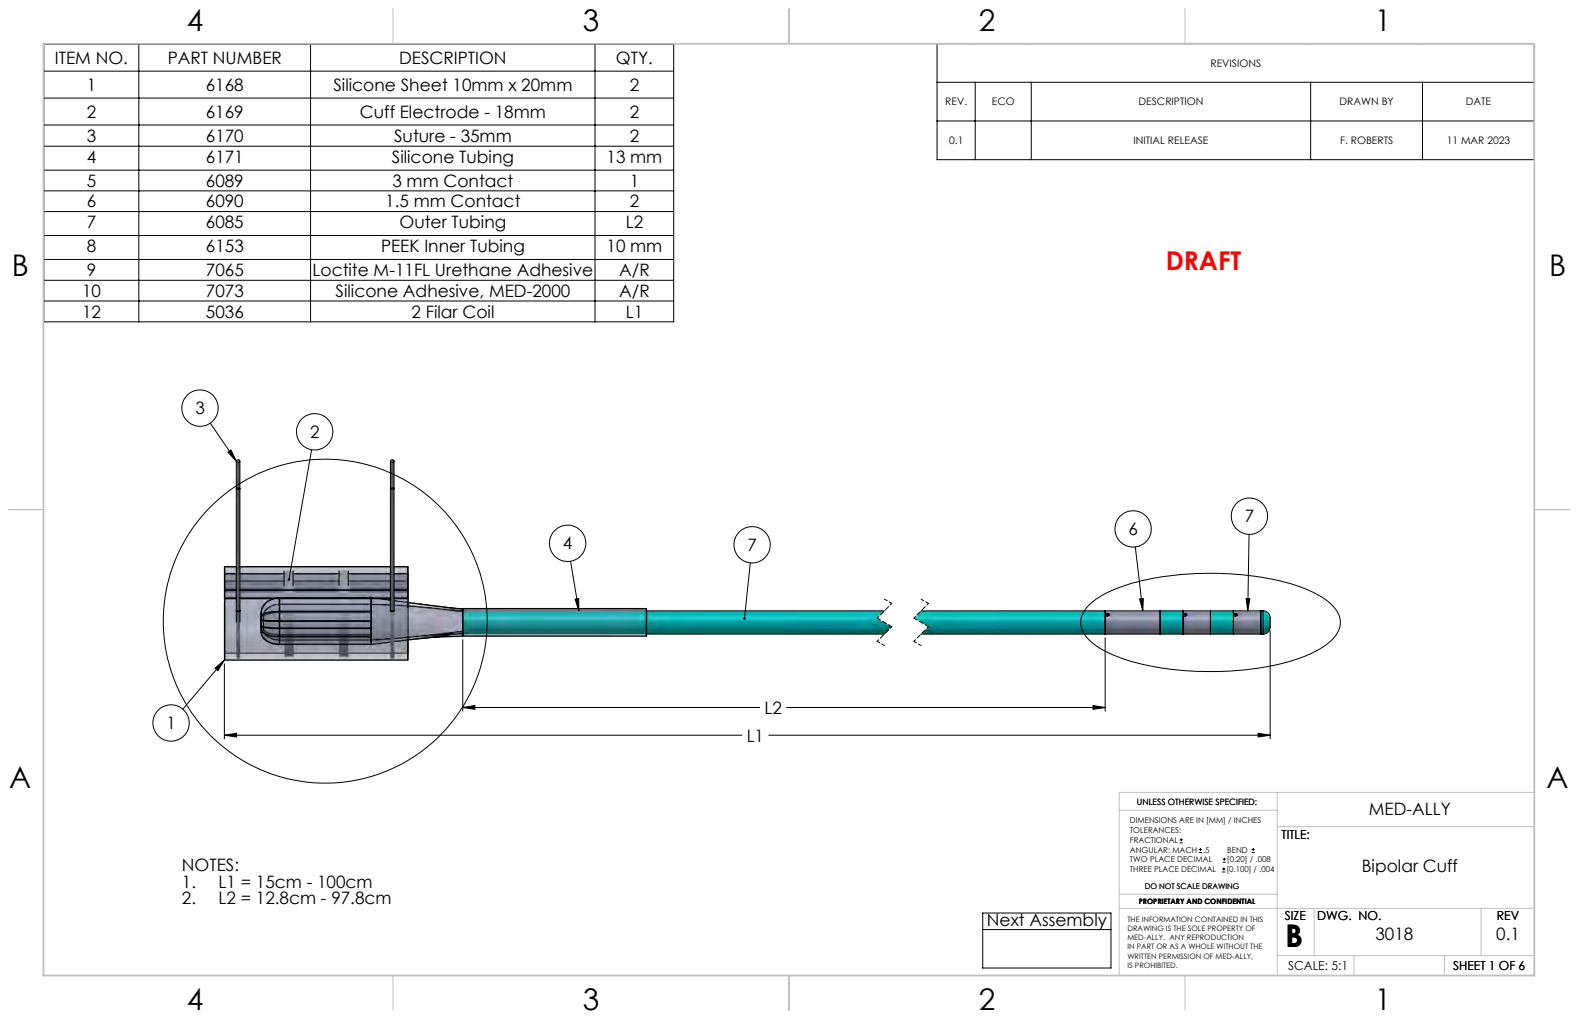
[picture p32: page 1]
NOTES: 1. L1 = 15cm - 100cm 2. L2 = 12.8cm - 97.8cm; TITLE:; ANGULAR: MACH .5; BEND; TWO PLACE DECIMAL; MED-ALLY; Next Assembly; Bipolar Cuff

1 | 6168 | Silicone Sheet 10mm x 20mm | 2
2 | 6169 | Cuff Electrode - 18mm | 2
3 | 6170 | Suture - 35mm | 2
4 | 6171 | Silicone Tubing | 13 mm
5 | 6089 | 3 mm Contact | 1
6 | 6090 | 1.5 mm Contact | 2
7 | 6085 | Outer Tubing | L2
8 | 6153 | PEEK Inner Tubing | 10 mm
9 | 7065 | Loctite M-11FL Urethane Adhesive | A/R
10 | 7073 | Silicone Adhesive, MED-2000 | A/R
12 | 5036 | 2 Filar Coil | L1

REV. | ECO | DESCRIPTION | DRAWN BY | DATE

0.1 | | INITIAL RELEASE | F. ROBERTS | 11 MAR 2023

UNLESS OTHERWISE SPECIFIED:
DIMENSIONS ARE IN [MM] / INCHES
TOLERANCES:
FRACTIONAL
THREE PLACE DECIMAL [0.100] / .004
DO NOT SCALE DRAWING
PROPRIETARY AND CONFIDENTIAL

THE INFORMATION CONTAINED IN THIS DRAWING IS THE SOLE PROPERTY OF MED-ALLY. ANY REPRODUCTION IN PART OR AS A WHOLE WITHOUT THE WRITTEN PERMISSION OF MED-ALLY, IS PROHIBITED. | SIZE SIZE B B | DWG. NO. DWG. NO. 3018 | REV REV 0.1

SCALE: 5:1 | | SHEET 1 OF 6

# DRAFT

B | B

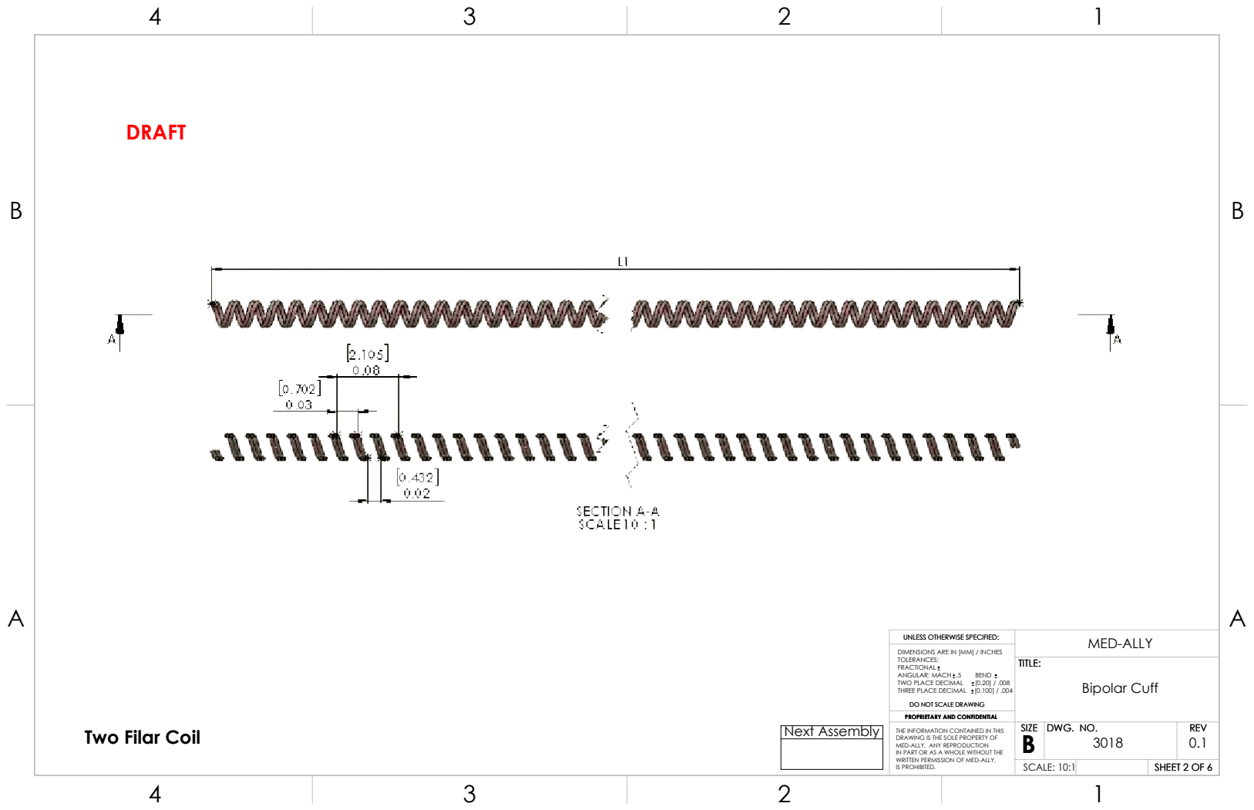
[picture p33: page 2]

# Two Filar Coil

DO NOT SCALE DRAWING

UNLESS OTHERWISE SPECIFIED:

THE INFORMATION CONTAINED IN THIS DRAWING IS THE SOLE PROPERTY OF | SIZE SIZE B B | DWG. NO. DWG. NO. 3018 | REV REV 0.1

## SCALE: 10:1

## TITLE:

PROPRIETARY AND CONFIDENTIAL

A | A

DO NOT SCALE DRAWING

UNLESS OTHERWISE SPECIFIED:

## TITLE:

DIMENSIONS ARE IN [MM] / INCHES TOLERANCES:
FRACTIONAL
ANGULAR: MACH .5 | BEND
TWO PLACE DECIMAL | [0.20] / .008
THREE PLACE DECIMAL [0.100] / .004

PROPRIETARY AND CONFIDENTIAL

# MED-ALLY

# Next Assembly

# Bipolar Cuff

# DRAFT

B | B

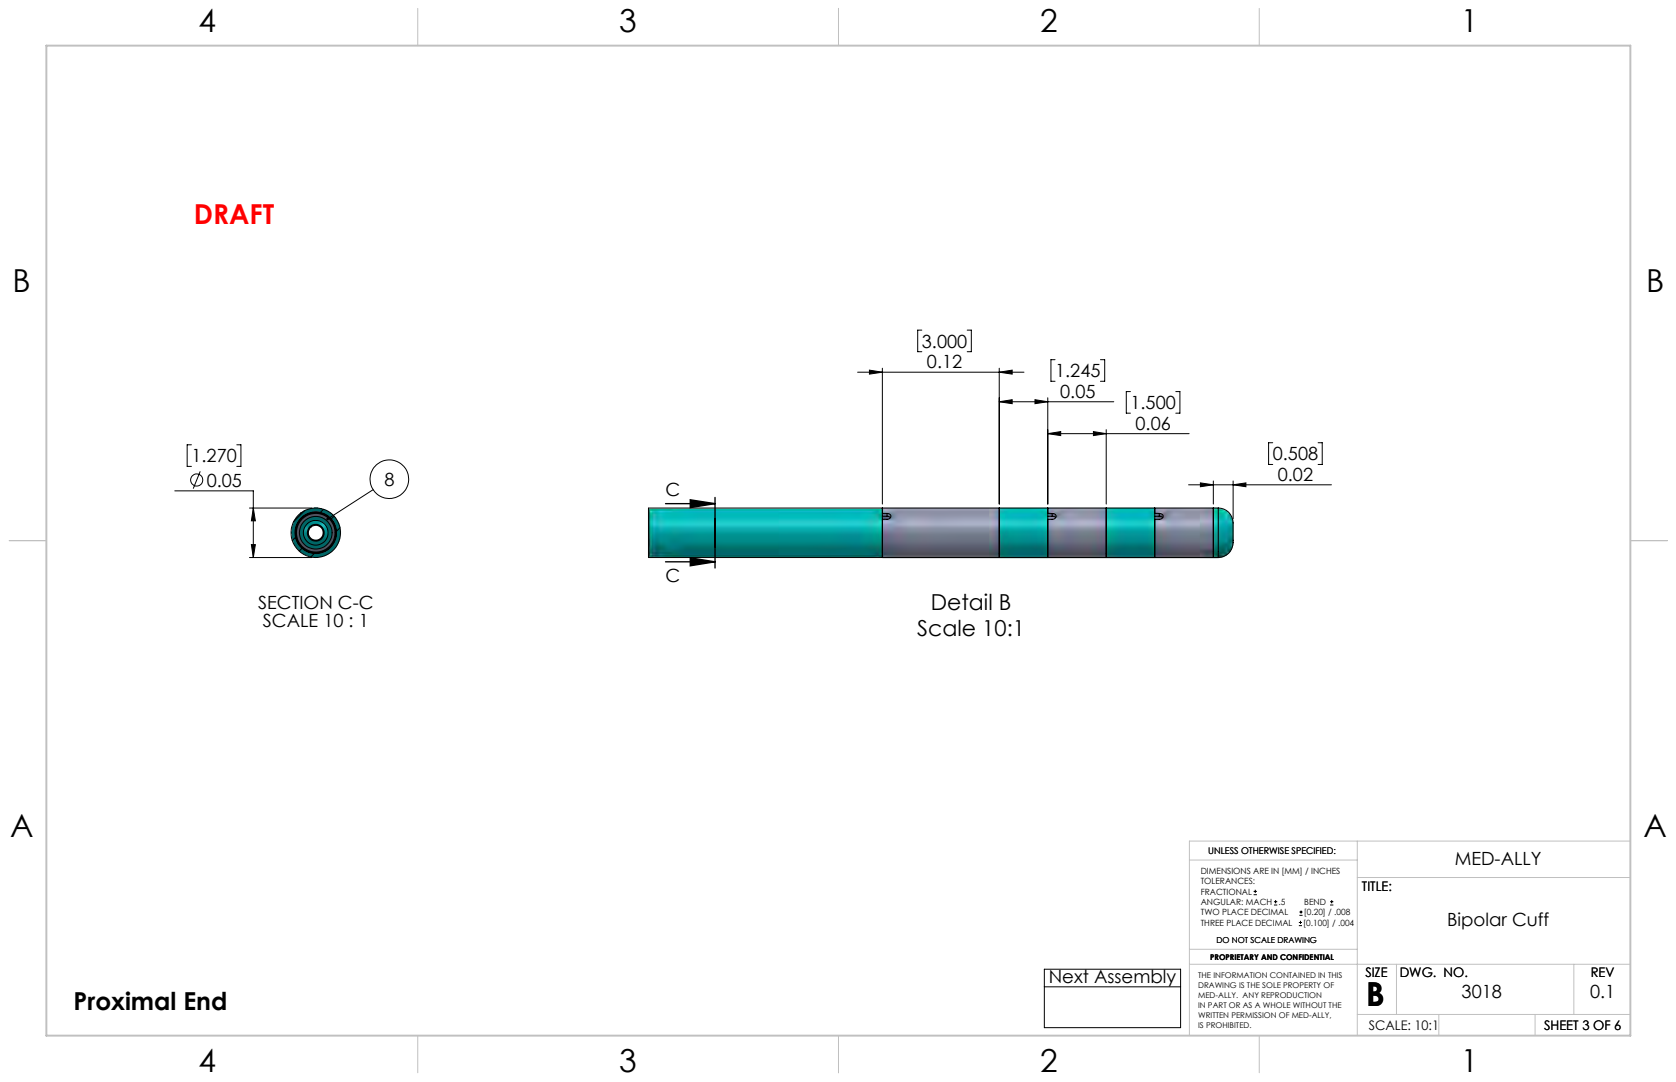
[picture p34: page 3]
SECTION C-C SCALE 10 : 1; Detail B Scale 10:1; Proximal End; TITLE:; ANGULAR: MACH .5; BEND; TWO PLACE DECIMAL; MED-ALLY; Next Assembly; Bipolar Cuff

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

SCALE: 10:1

# DRAFT

B | B

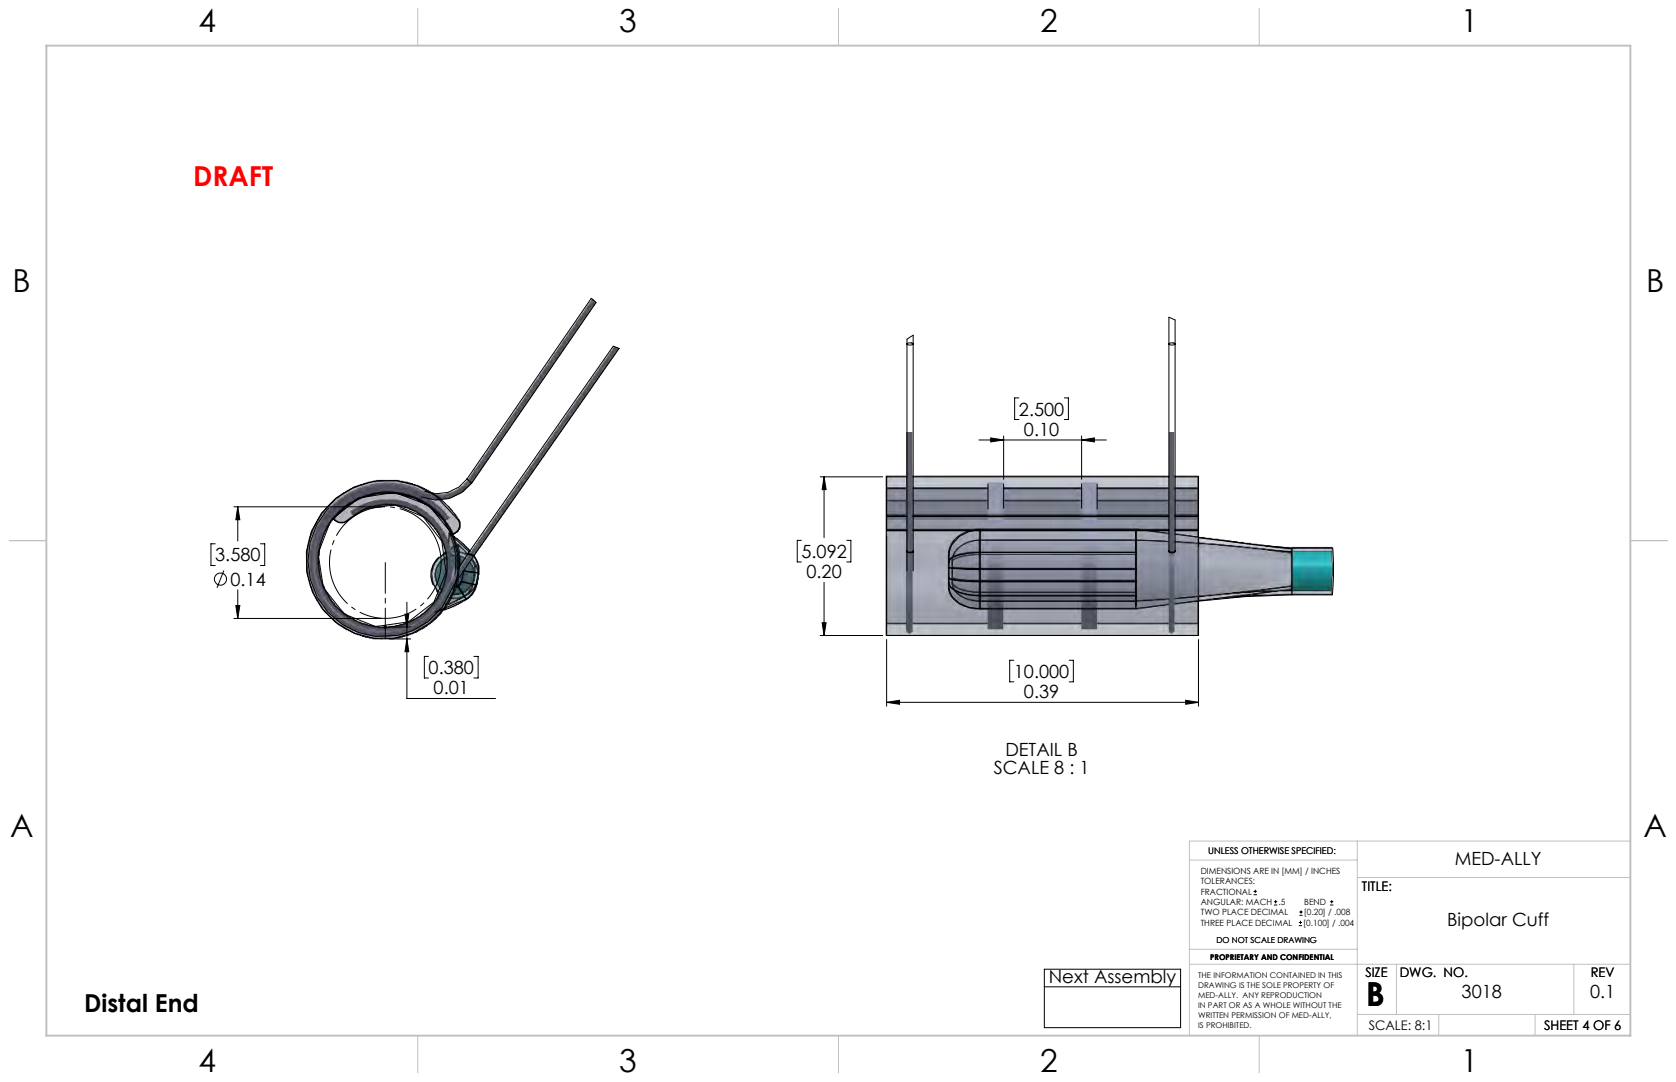
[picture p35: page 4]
DETAIL B SCALE 8 : 1; Distal End; TITLE:; ANGULAR: MACH .5; BEND; TWO PLACE DECIMAL; MED-ALLY; Next Assembly; Bipolar Cuff

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

SCALE: 8:1

20.000
0.79

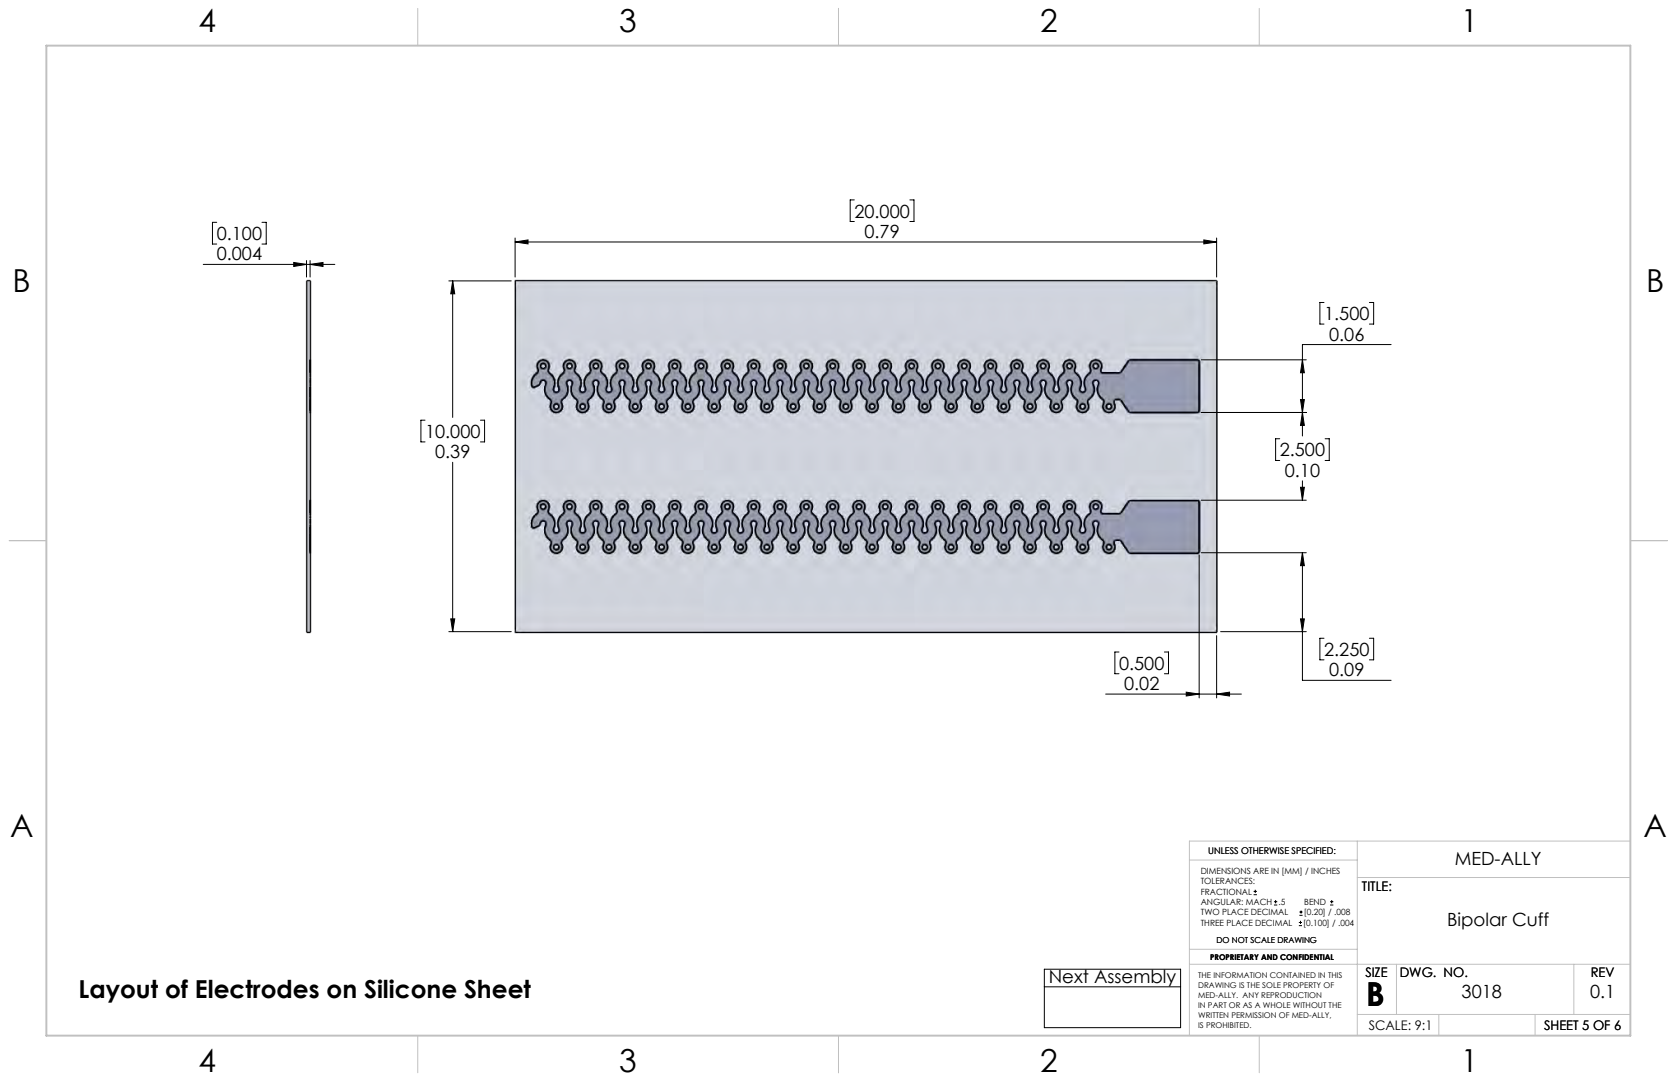
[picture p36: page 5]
TITLE:; ANGULAR: MACH .5; BEND; TWO PLACE DECIMAL; MED-ALLY; Next Assembly; Bipolar Cuff

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

Layout of Electrodes on Silicone Sheet

SCALE: 9:1

# DRAFT

B | B

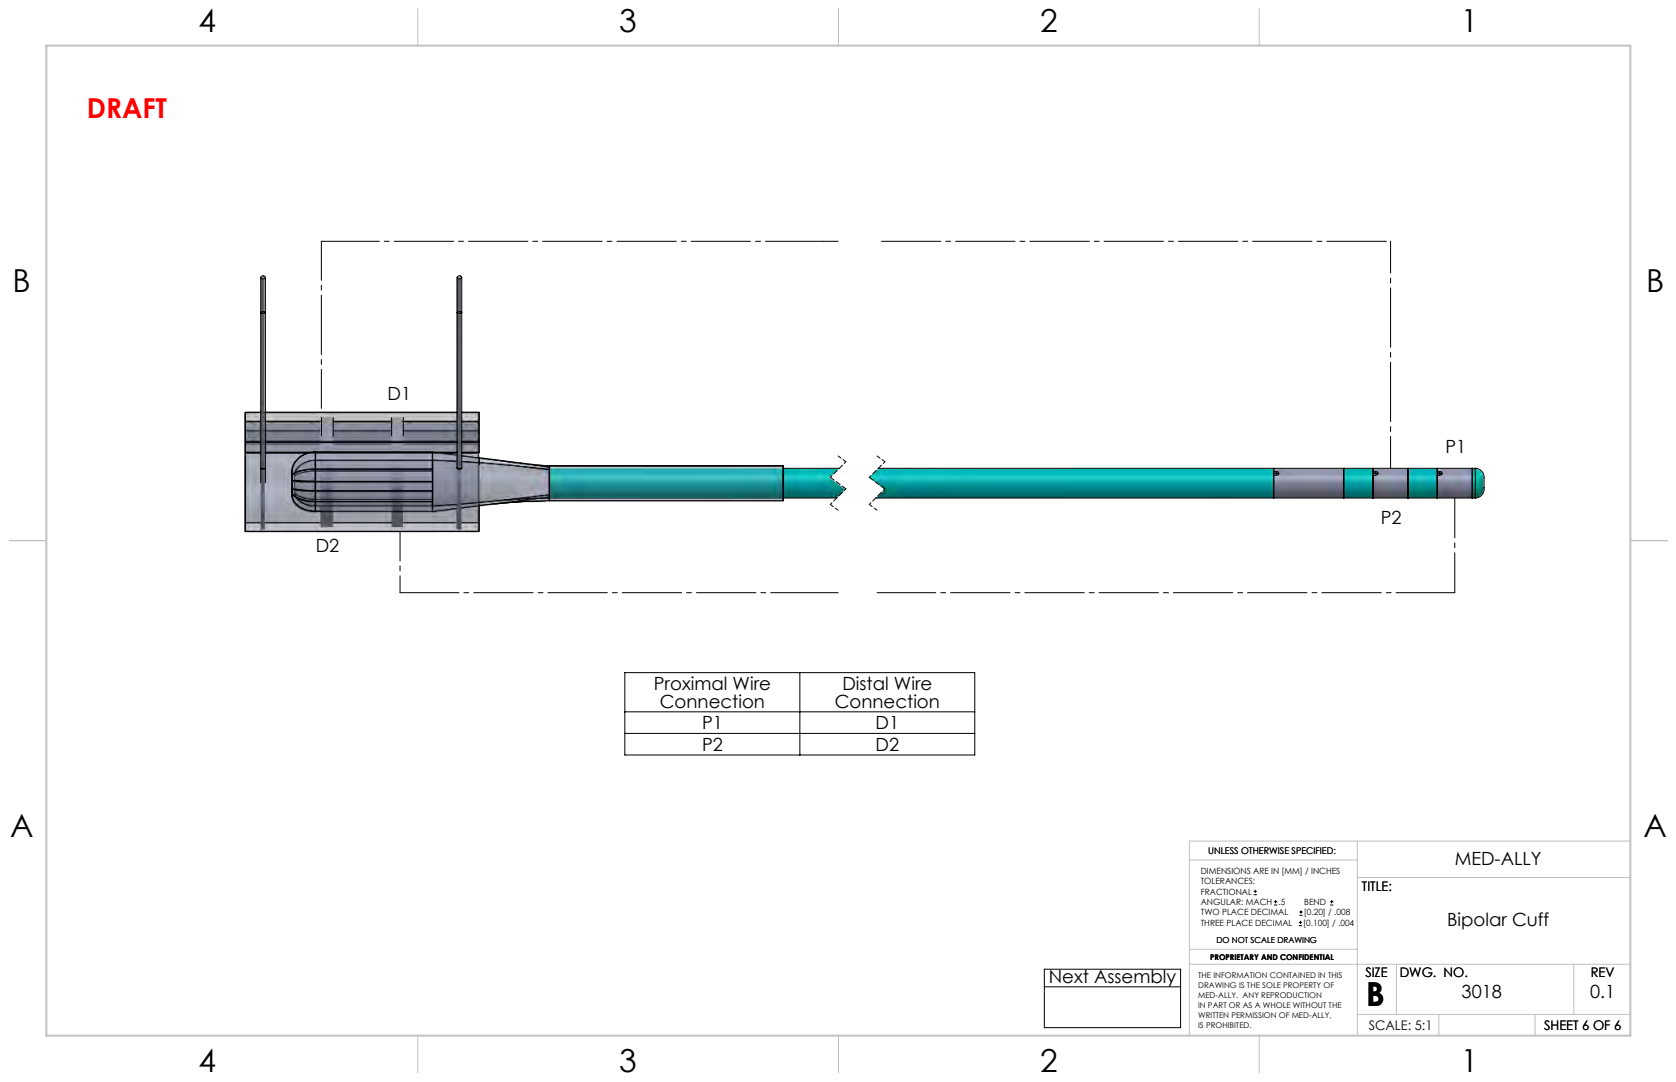
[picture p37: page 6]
TITLE:; ANGULAR: MACH .5; BEND; TWO PLACE DECIMAL; MED-ALLY; Next Assembly; Bipolar Cuff

Proximal Wire Connection | Distal Wire Connection
P1 | D1
P2 | D2

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

SCALE: 5:1

L3 | L2

L1

REV. | ECO | DESCRIPTION | DRAWN BY | DATE

0.1 | | INITIAL RELEASE | F. ROBERTS | 15 MAR 2023

ITEM NO. | PART NUMBER | DESCRIPTION | QTY.
1 | 6089 | Proximal Contact - 3mm | 1
2 | 6085 | Outer Tubing | L2, L3
3 | 6090 | Proximal Contact - 1.5 mm | 2
5 | 6175 | Distal Suture Tip | 1
6 | 6176 | Suture Sleeve | 1
7 | 6081-3 | Electrode, 3mm | 2
8 | 6153 | PEEK Single Lumen Tube | 9mm

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

THE INFORMATION CONTAINED IN THIS DRAWING IS THE SOLE PROPERTY OF | SIZE SIZE B B | DWG. NO. DWG. NO. 3020 | REV REV 0.1

SCALE: 7:1

B | B
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

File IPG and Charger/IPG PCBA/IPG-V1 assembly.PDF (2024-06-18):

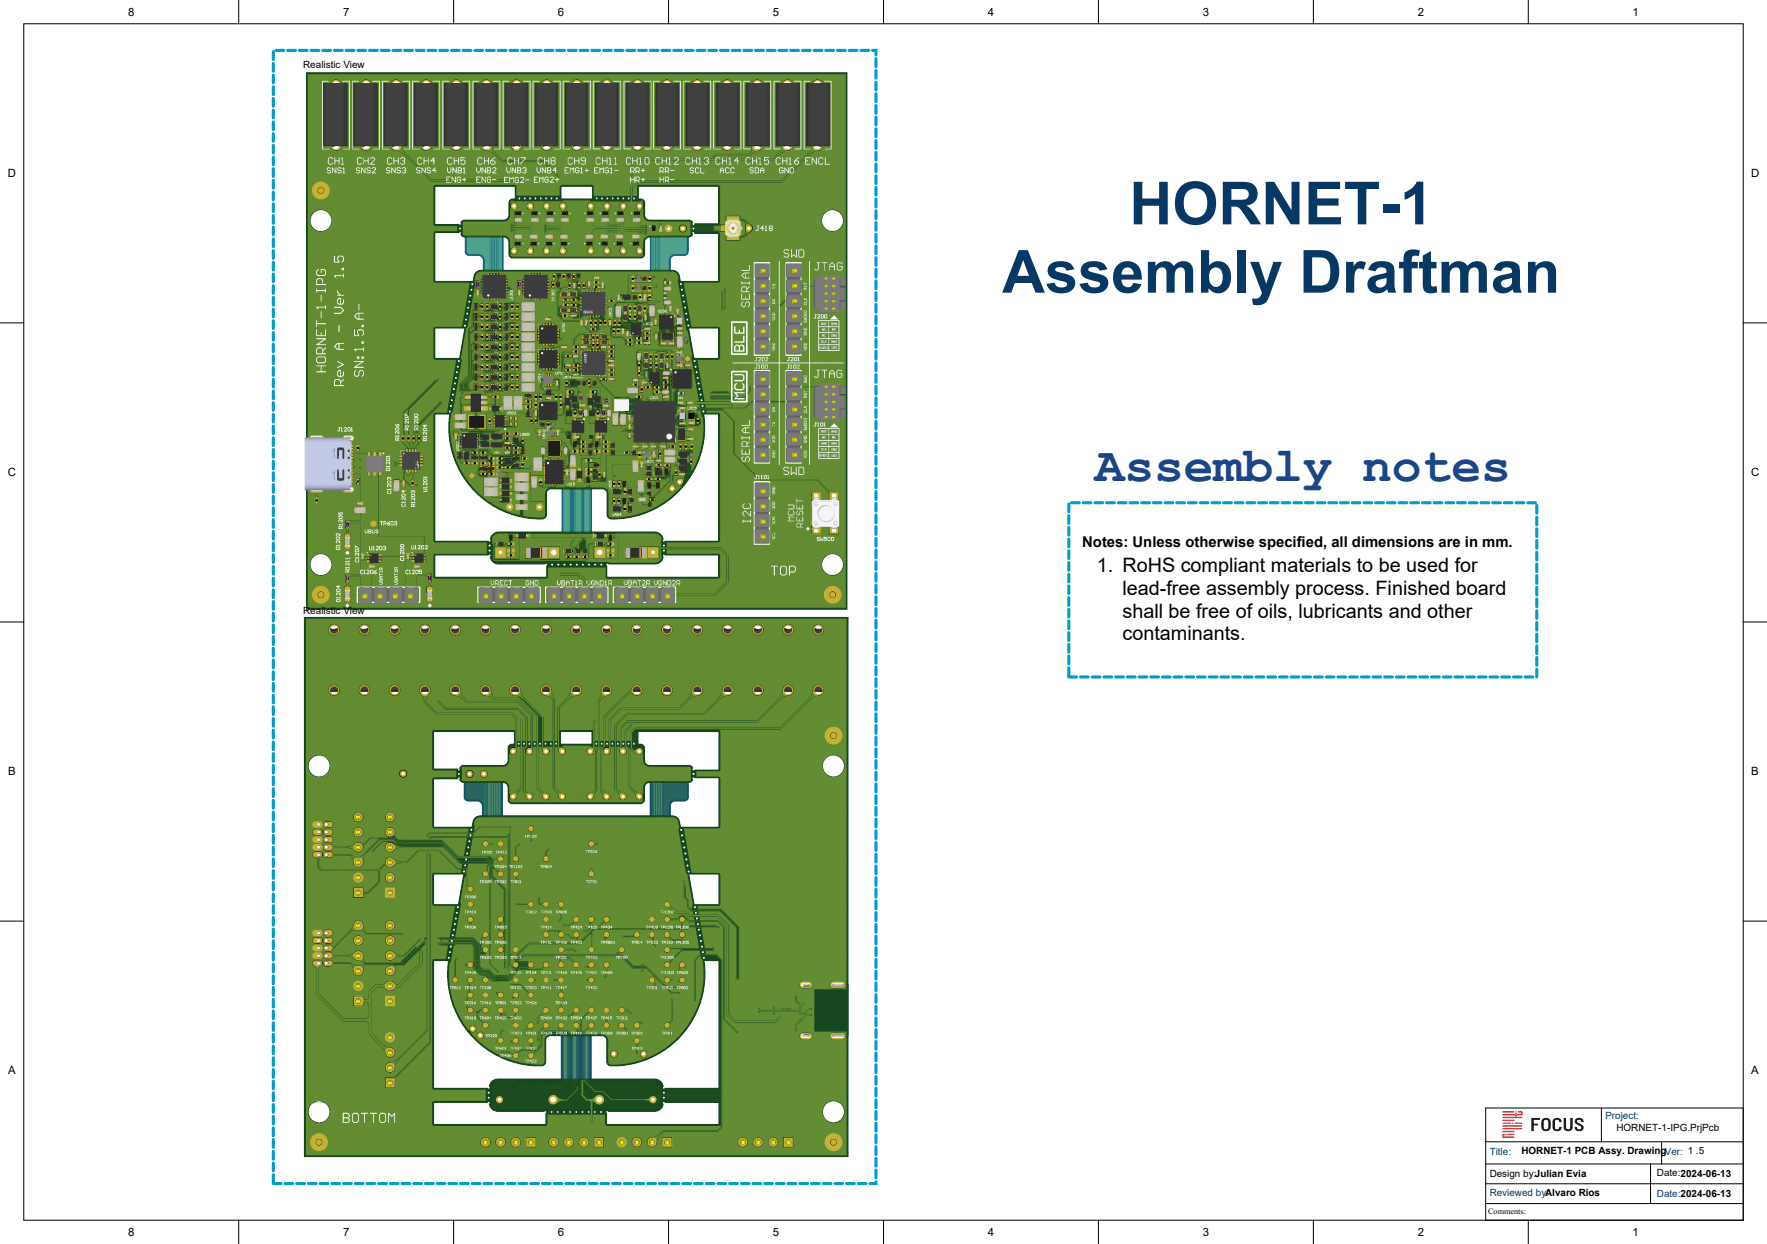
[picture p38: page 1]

Notes: Unless otherwise specified, all dimensions are in mm.
RoHS compliant materials to be used for
lead-free assembly process. Finished board
shall be free of oils, lubricants and other
contaminants.

Project: HORNET-1-IPG.PrjPcb

Title: HORNET-1 PCB Assy. Drawing | Ver: 1

Design by: Julian Evia | Date: 2024-06-13
Reviewed by: Alvaro Rios | 2024-06-13

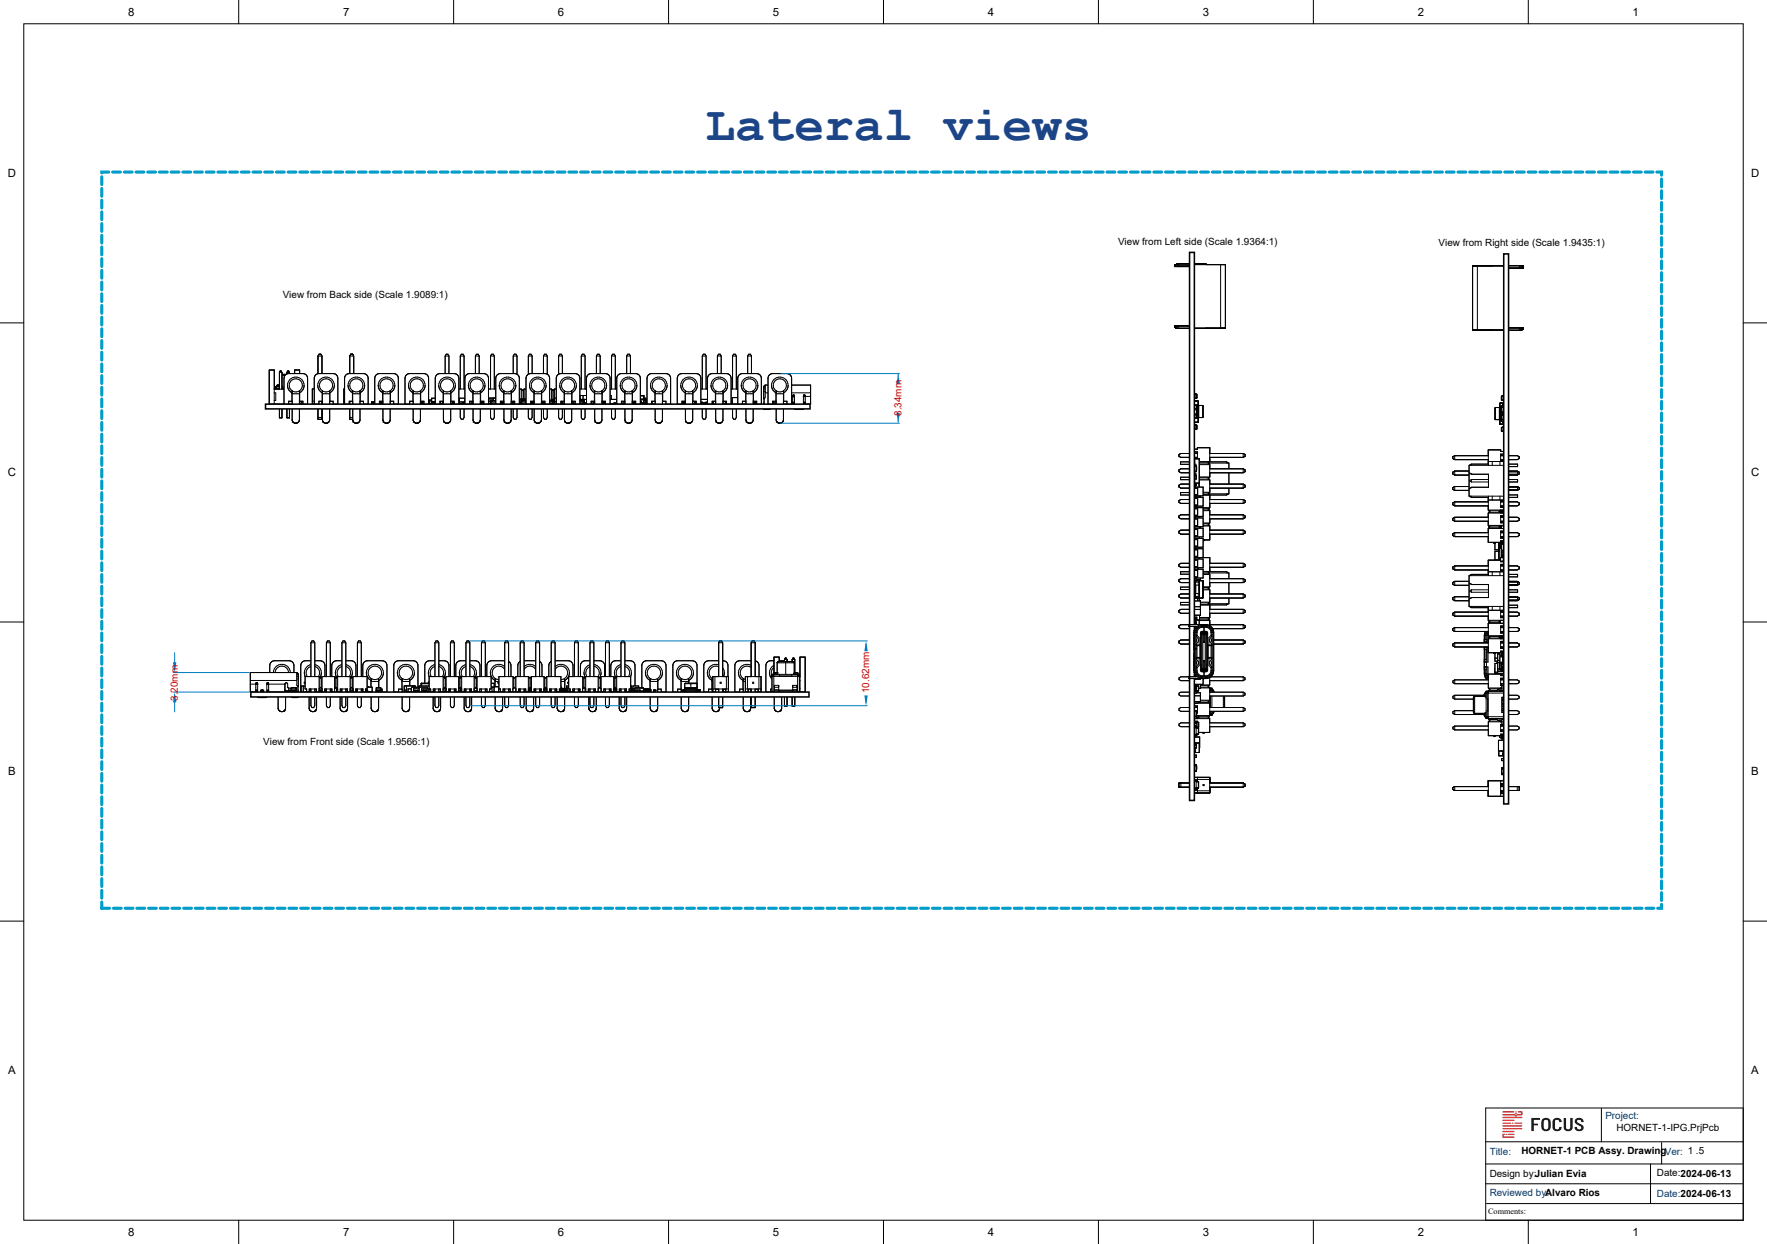
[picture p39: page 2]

View from Back side (Scale 1.9089:1)

View from Front side (Scale 1.9566:1)

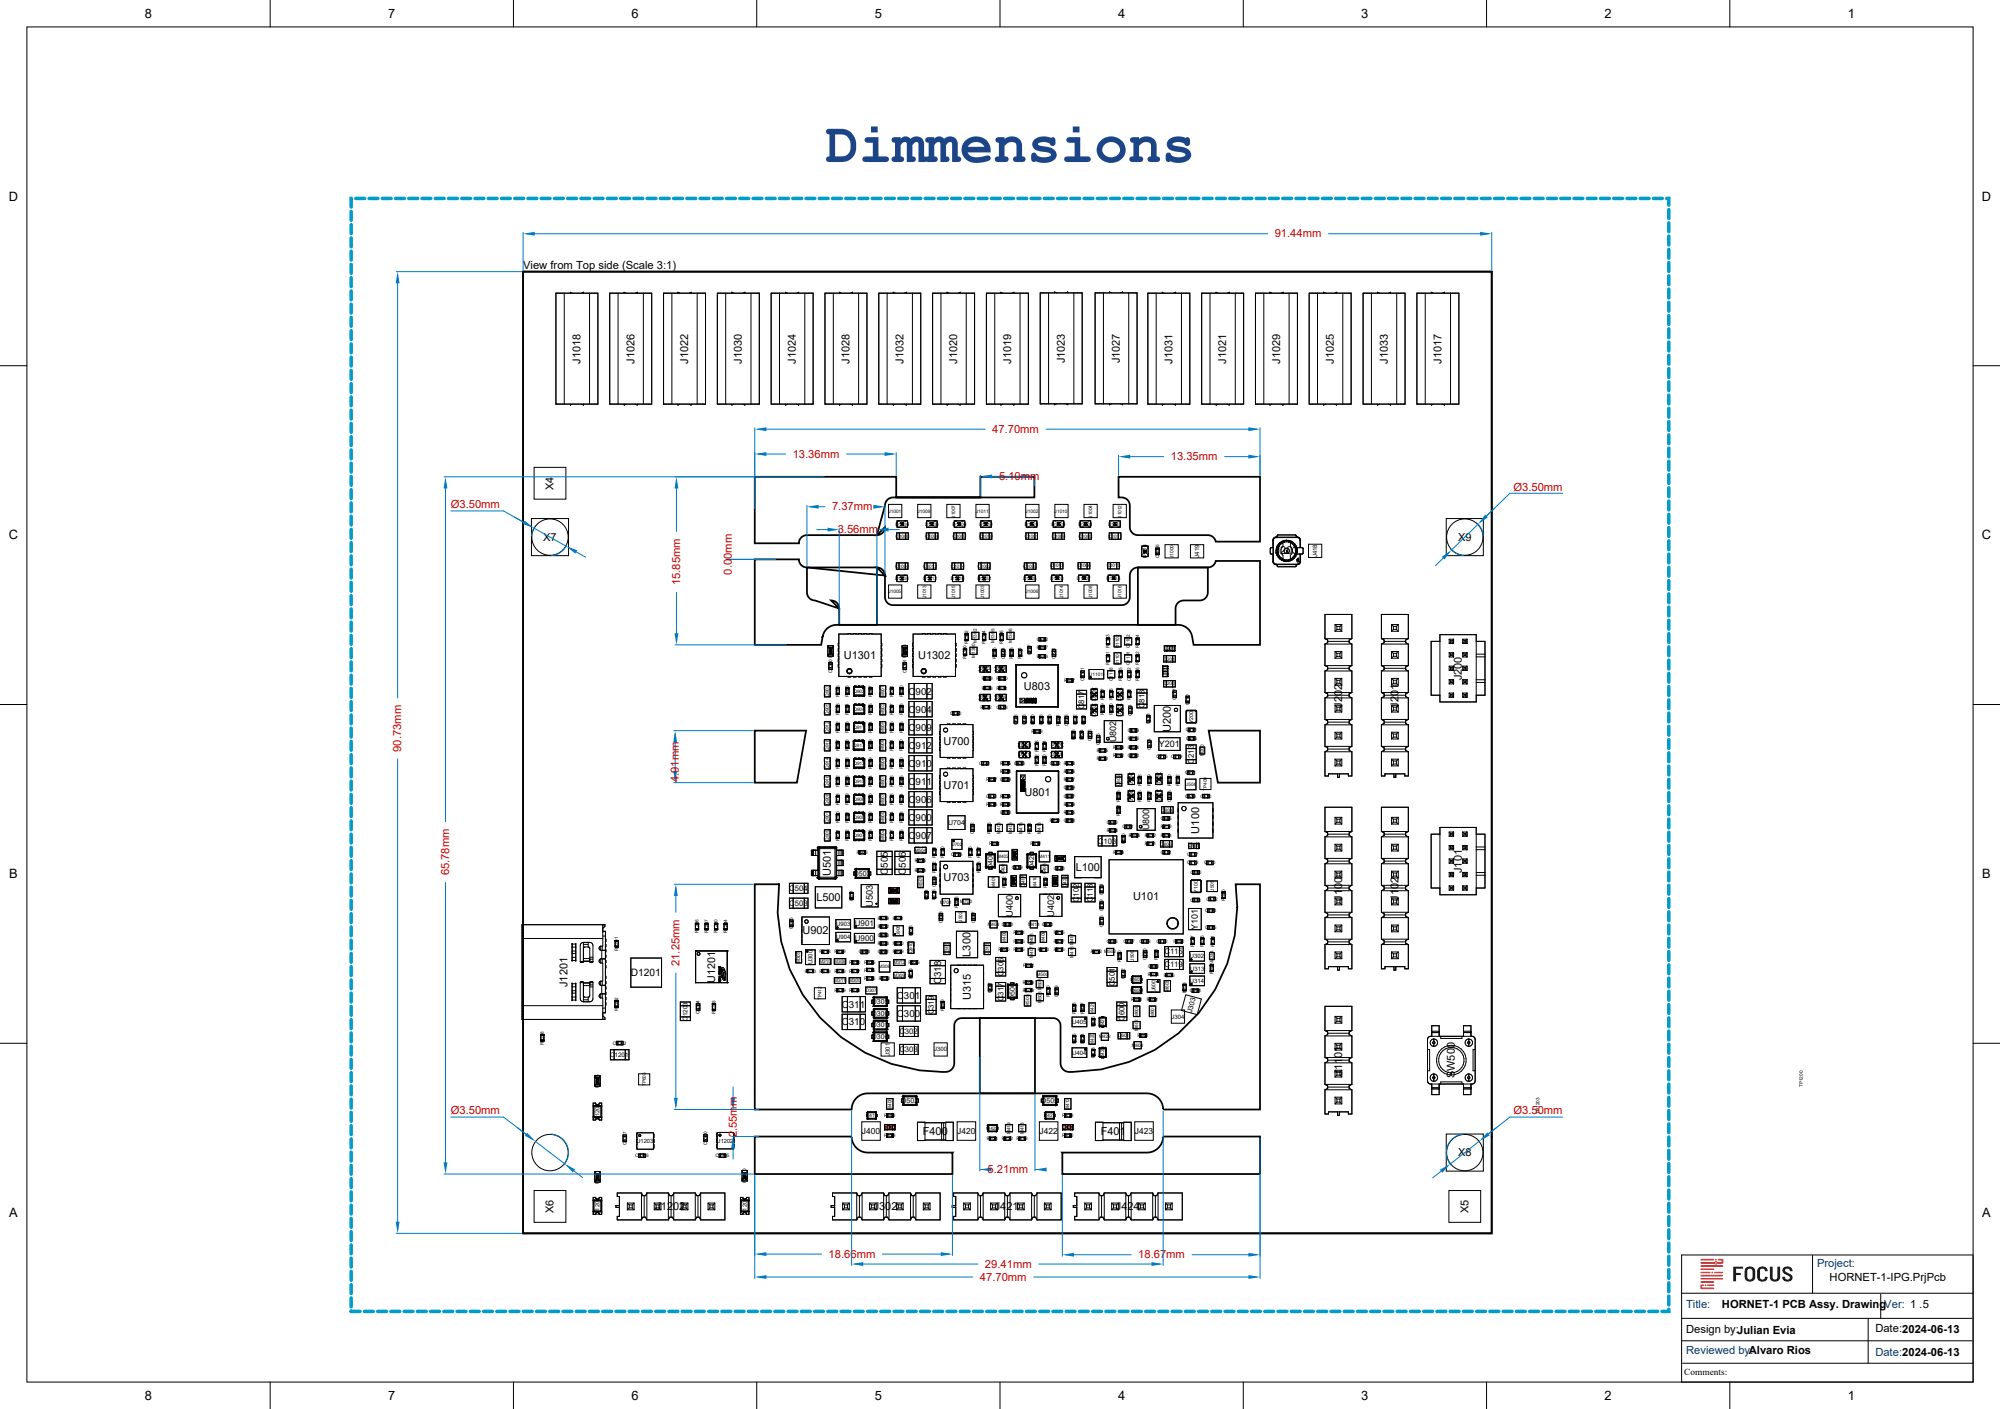
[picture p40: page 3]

View from Top side (Scale 3:1)

HORNET-1 PCB Assy. Drawing

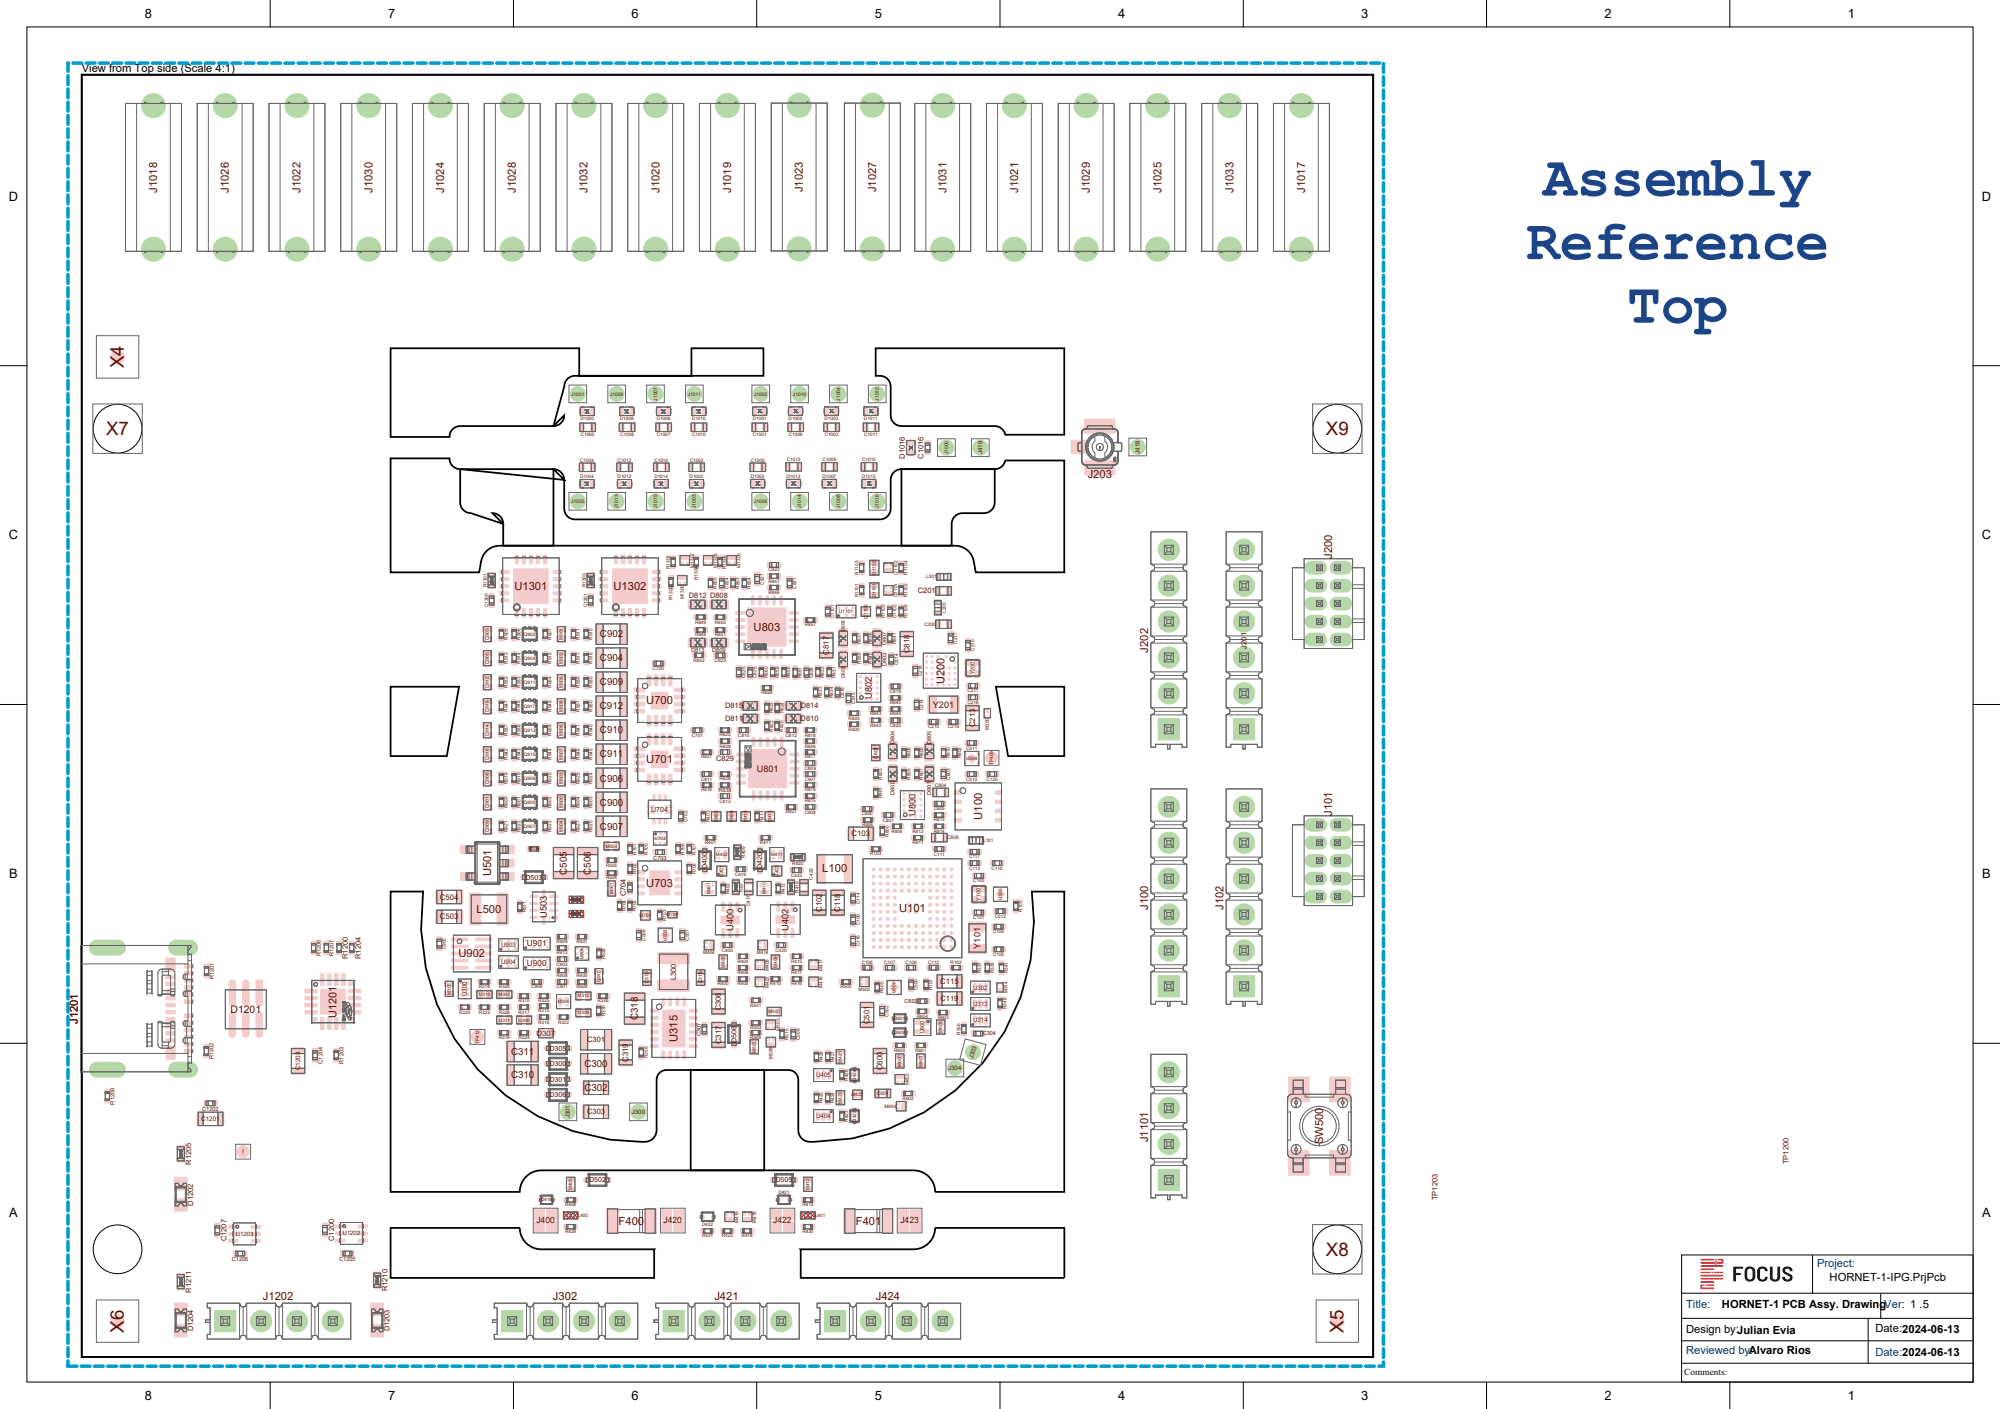
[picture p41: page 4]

View from Top side (Scale 4:1)


View from Bottom side (Scale 4:1)

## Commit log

2024-04-23 Add files via upload
    Added STEP files for manifest test
    [B3- Large.STEP, B3- Small.STEP, E3- Large.STEP, E3- Small.STEP]
2024-04-23 Create manifest.json
    First pass at creating a manifest file linking to different electrode CAD models in OpenNerve, starting with the PxC electrodes
2024-06-18 Rename IPG and Charger/IPG PCBA/IPG-V1 rev0.24 BOM.xlsx to IPG and Charger/IPG PCBA/Archived/IPG-V1 rev0.24 BOM.xlsx
    [IPG-V1 rev0.24 BOM.xlsx]
2024-06-18 Rename IPG and Charger/IPG PCBA/IPG-V1 3D.PDF to IPG and Charger/IPG PCBA/Archived/IPG-V1 3D.PDF
2024-06-18 Rename IPG and Charger/IPG PCBA/IPG-V1 PCB Assembly.PDF to IPG and Charger/IPG PCBA/Archived/IPG-V1 PCB Assembly.PDF
2024-06-18 Rename IPG and Charger/IPG PCBA/IPG-V1.pdf to IPG and Charger/IPG PCBA/Archived/IPG-V1.pdf
2024-06-18 Rename IPG and Charger/IPG PCBA/Source Files (Altium)/IPG-V1 layout.step to IPG and Charger/IPG PCBA/IPG-V1.step
    [IPG-V1.step]
2024-06-19 Rename Physical Sensors/Strain Sensor/images/README.md to Physical Sensors/Strain Sensor/Archived/images/README.md
2024-06-19 Rename Physical Sensors/Strain Sensor/Strain sensor charaterization and encapsulation 20230710.pdf to Physical Sensors/Strain Sensor/Archived/Strain sensor charaterization and encapsulation 20230710.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
2024-06-19 Rename Physical Sensors/Strain Sensor/Strain Sensor-Alpha Stretch Strain Sensor SpecSheet.pdf to Physical Sensors/Strain Sensor/Archived/Strain Sensor-Alpha Stretch Strain Sensor SpecSheet.pdf
2024-06-19 Rename Physical Sensors/Temperature Sensor/CAD Design for Temperature Sensor.pdf to Physical Sensors/Temperature Sensor/Archived/CAD Design for Temperature Sensor.pdf
2024-06-19 Rename Physical Sensors/Temperature Sensor/Temperature Sensor-Temperature Sensor Characterization.pdf to Physical Sensors/Temperature Sensor/Archived/Temperature Sensor-Temperature Sensor Characteriz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
2024-06-19 Rename Physical Sensors/Temperature Sensor/Temperature Sensor-Temperature Sensor Images and Fabrication Protocol.pdf to Physical Sensors/Temperature Sensor/Archived/Temperature Sensor-Temperature Sen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
2024-06-19 Rename Chemical Sensors/Thin Film Electrode Design/Connector_PCB.pdf to Chemical Sensors/Thin Film Electrode Design/Archived/Connector_PCB.pdf
2024-06-19 Rename Chemical Sensors/Thin Film Electrode Design/HORNET_1v0.3 PIEFClean.pdf to Chemical Sensors/Thin Film Electrode Design/Archived/HORNET_1v0.3 PIEFClean.pdf
2024-06-19 Update and rename Chemical Sensors/Thin Film Electrode Design/HORNET_1v0.3 PIEFclean.dxf to Chemical Sensors/Thin Film Electrode Design/Archived/HORNET_1v0.3 PIEFclean.dxf
    [HORNET_1v0.3 PIEFclean.dxf]
2024-06-19 Update and rename Chemical Sensors/Thin Film Electrode Design/HORNET_2v0.3 PIEFClean.dxf to Chemical Sensors/Thin Film Electrode Design/Archived/HORNET_2v0.3 PIEFClean.dxf
    [HORNET_2v0.3 PIEFClean.dxf]
2024-06-19 Rename Chemical Sensors/Thin Film Electrode Design/HORNET_2v0.3 PIEFClean.pdf to Chemical Sensors/Thin Film Electrode Design/Archived/HORNET_2v0.3 PIEFClean.pdf
2024-06-19 Rename Chemical Sensors/Electrochemical Characterization and Surface Modification-2.pdf to Chemical Sensors/Archived/Electrochemical Characterization and Surface Modification-2.pdf
2024-06-19 Rename Chemical Sensors/Fabrication of Echem Sensors.pdf to Chemical Sensors/Archived/Fabrication of Echem Sensors.pdf
2024-06-19 Rename Parylene Cuff Electrode/Fabrication and Packaging/Full Fabrication Protocol (Rev 1).pdf to Parylene Cuff Electrode/Fabrication and Packaging/Archived/Full Fabrication Protocol (Rev 1).pdf
2024-06-19 Rename Parylene Cuff Electrode/Fabrication and Packaging/Thin Film Fabrication Protocol (Rev 1).pdf to Parylene Cuff Electrode/Fabrication and Packaging/Archived/Thin Film Fabrication Protocol (Rev 1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
2024-06-19 Rename Parylene Cuff Electrode/Design/SLDPRT Files/B3- Large.SLDPRT to Parylene Cuff Electrode/Design/SLDPRT Files/Archived/B3- Large.SLDPRT
    [B3- Large.SLDPRT]
2024-06-19 Rename Parylene Cuff Electrode/Design/SLDPRT Files/B3- Small.SLDPRT to Parylene Cuff Electrode/Design/SLDPRT Files/Archived/B3- Small.SLDPRT
    [B3- Small.SLDPRT]
2024-06-19 Rename Parylene Cuff Electrode/Design/SLDPRT Files/E3- Large.SLDPRT to Parylene Cuff Electrode/Design/SLDPRT Files/Archived/E3- Large.SLDPRT
    [E3- Large.SLDPRT]
2024-06-19 Rename Parylene Cuff Electrode/Design/SLDPRT Files/E3- Small.SLDPRT to Parylene Cuff Electrode/Design/SLDPRT Files/Archived/E3- Small.SLDPRT
    [E3- Small.SLDPRT]
2024-06-19 Update and rename Parylene Cuff Electrode/Design/STEP Files/B3- Large.STEP to Parylene Cuff Electrode/Design/STEP Files/Archived/B3- Large.STEP
    [B3- Large.STEP]
2024-06-19 Update and rename Parylene Cuff Electrode/Design/STEP Files/B3- Small.STEP to Parylene Cuff Electrode/Design/STEP Files/Archived/B3- Small.STEP
    [B3- Small.STEP]
2024-06-19 Update and rename Parylene Cuff Electrode/Design/STEP Files/E3- Large.STEP to Parylene Cuff Electrode/Design/STEP Files/Archived/E3- Large.STEP
    [E3- Large.STEP]
2024-06-19 Update and rename Parylene Cuff Electrode/Design/STEP Files/E3- Small.STEP to Parylene Cuff Electrode/Design/STEP Files/Archived/E3- Small.STEP
    [E3- Small.STEP]
